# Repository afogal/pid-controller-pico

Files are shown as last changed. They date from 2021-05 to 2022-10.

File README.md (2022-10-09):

# pid-controller-pico

## Setup

### Command

To install prerequisites:

```sh 
sudo pip3 -H install pyqt5 pyqtgraph
```

### Mosquitto (MQTT Broker)

Install mosquitto:

` sudo apt install mosquitto `

To run mosquitto in verbose mode:

` mosquitto -c mosquitto.conf -v `

To ensure it runs on startup (and run it now):

` sudo systemctl enable mosquitto && sudo systemctl start mosquitto `

You also have to copy the `mosquitto.conf`:

` sudo cp mosquitto.conf /etc/mosquitto/mosquitto.conf `

### RPi Pico

To setup the pico fresh, hold down the bootsel button and plug it into the computer. Download the latest adafruit circuitpython uf2 and the latest circuitpython library bundle. (Make sure the versions match, a new major revision is coming out soon, I used the old one, version 6.x.x). Then, drag and drop the circuitpython uf2 to the pico, it'll then remount itself. Now the pico will show up as a drive. Drag and drop the following files to the `lib` folder:

Folders:
* `adafruit_bus_device`
* `adafruit_minimqtt`
* `adafruit_wiznet5k`
* `adafruit_ads1x15`

Files:
* `adafruit_requests.mpy`
* `adafruit_mcp4725.mpy`

As for wiring, the ethernet is wired as follows (diagram and other documentationshows the ethernet interface as WIZ820io, but the prototype that Alex constructed in Spring 2021 used WIZ850io --- JDDM).

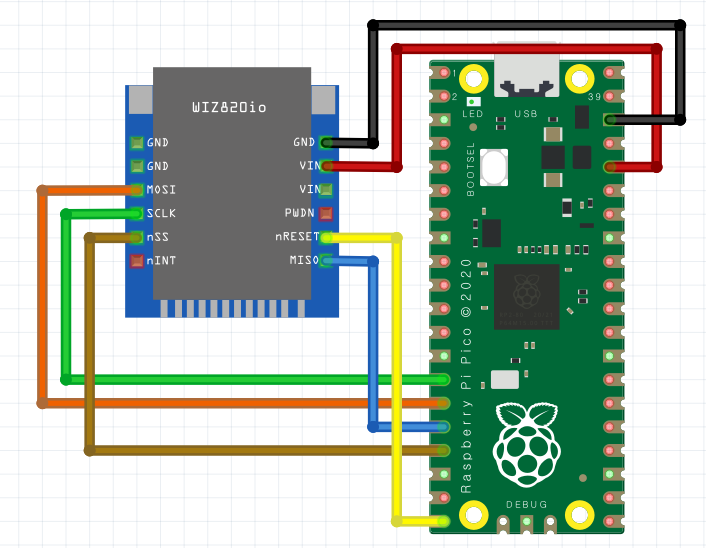
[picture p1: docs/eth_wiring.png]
eth wiring


The i2c bus is wired: pin 26 (GP20) - SDA, pin 27 (GP21) - SCL, and of course, ground to ground and 3v3 to 3v3.

See also: [Schematic](docs/schematic.pdf) and [PCB Layout](docs/pcb.pdf).

In order to program the pico, all you have to do is copy the code.py to the pico, and it will then run that code on boot. One can also install the Thonny editor or the Mu editor. To one can then set Thonny to "Micropython" and point it at the correct serial port (com4 for me) and then you get a REPL running on the pico!

## Settings (defaultSettings dictionary)

The meaning of each entry in the defaultSettings dicitonary is as follows:
* `'setCurrent':0` (Amps) the amount of current to output
* `'setTemp':25` (deg C) the current set temperature to hold
* `'Kc': 6.0787` (W/deg C) PID proportional gain
* `'Ti':330` (sec) PID integration time
* `'Td':0` (sec) PID derivative time (zero gives only a PI control)
* `'I_max':4` (W^2) Maximum value of the I term in PID (best left at max power, 0 -> disabled) 
* `'loadResist':1` (ohm) resistance of the load resistor
* `'maxTemp':150` (deg C) max temperature of the load
* `'maxCurr':2.0` (Amps) max current the load can withstand
* `'maxResVolt':5` (Volt) voltage indicating max resistance
* `'maxRes':13` (kohms) max resistance at max voltage
* `'maxSuppCurrVolt':5` (Volt) the voltage signal that will cause max current from the supply
* `'maxSuppCurr':2` (Amps) max current given by max voltage
* `'thermBeta':3380` (kelvin) thermistor beta
* `'thermR25':10` (kohm) resistance of thermistor at 25 degC
* `'outputToggle':0` are we outputting?
* `'filterHz':1` (Hz) block freqencies higher than this
* `'period':0.016666667` (sec) how often to update PID
* `'constCurr':False` (bool) are we running constant current or PID temperature?
* `'maxErrorLen':100` (int) how many terms to keep around for error
* `'freqAnalysis':False` (bool) outputs current following a cosine wave, only really used for a specific sort of PID tuning
* `'reportMode':'mean'` (one of 'mean', 'latest') report the temperature and current as either the mean of all values since the last or just the latest values
* `'user':'pico'` MQTT username for the PID controller
* `'password':'password'` MQTT password for the PID controller
* `'serverIP':"192.168.0.100"` IP address of the MQTT broker
* `'mqttDelay':5e8` (nsec) how often to poll for mqtt messages and send the current state
* `'mqttReconn":300e8` (nsec) how often to attempt reconnecting to MQTT (is slow, don't attempt often)
* `'lcdRefresh':2.5e8` (nsec) how often to refresh the lcd screen

## User Interface:

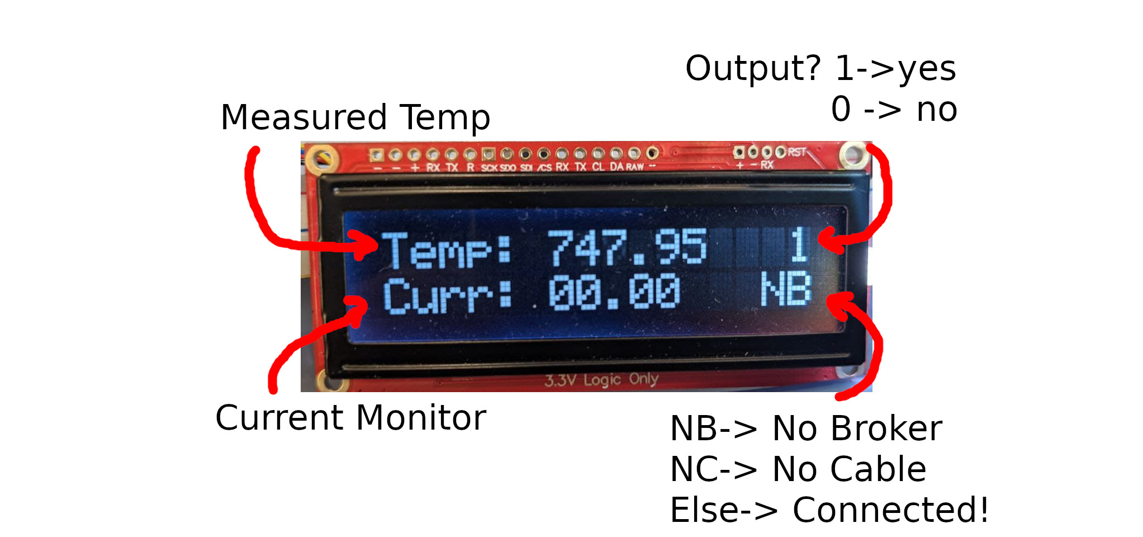
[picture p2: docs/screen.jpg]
screen


## Control UI:

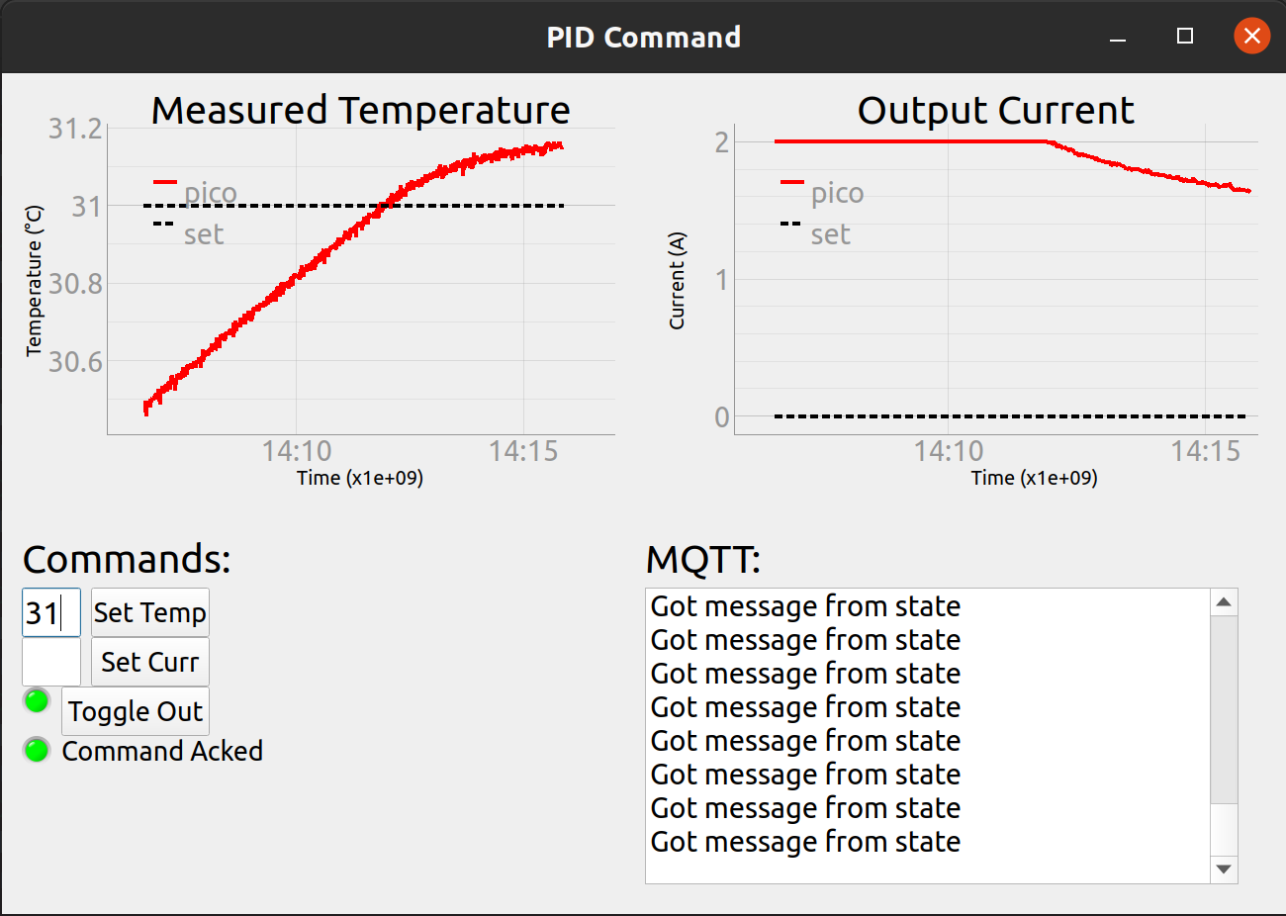
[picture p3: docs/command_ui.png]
control ui


This is the remote command window, featuring set temperature command, set current command, and a toggle output command. For the indicator next to toggle out, red means no current being outputted, and green means current being outputted. The "Command Acked" indicator shows whether or not the pico has recieved and replied to whatever the latest command was, red meaning no, green meaning yes. 

In the bottom right is a text window which updates when acks and messages are recieved, and it will also display errors from trying to type text into the set temp and set curr boxes. 

Finally, in the top is two graphs, they can be panned and zoomed at will, and update with the latest and greatest data from the pico. 

The ui has some configurable parameters, which can be found near the top of [server.py](server/server.py), which include what username the server is, what username the pico is, a password for the mqtt broker, and the IP of the mqtt broker. The broker and command need not be run on the same device, but they can be. 

## Notes:

* printing (which prints to serial) puts a lot of delay (and sometimes doesnt work at all)
* you might have to reconfigure the IP and gatway of the pico depending on network architecture. Run `ipconfig` on windows or `ip addr` on linux to find the relevant details
* the MQTT client keep\_alive is (for some really dumb reason) used as the default pingresp timeout, which means you either flood the broker with ping requests or you wait forever (with no PID processing in the meantime) if the broker ever goes down. I thought 5 seconds would be a fair tradeoff. Even worse: keep\_alive is used as the default recieving timeout, so we can't set it extremely low either. I thought it would be better not to edit and recompile the adafruit library to remedy this, but if desired it would be quite easy.
* for whatever reason, *sometimes* the ADC reads anything greater than 4.1V as exactly 4.1V, I think this is a referencing issue, but it doesn't always come up. This corresponds to a current of 1.64A.

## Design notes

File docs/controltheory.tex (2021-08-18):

\documentclass[11pt, letterpaper]{article}
\usepackage[utf8]{inputenc}
\usepackage{graphicx}
\usepackage{indentfirst}
\usepackage{float}
\setlength{\parindent}{5ex}
\renewcommand{\arraystretch}{1.2}

\usepackage{geometry}

\begin{document}

\begin{titlepage}
    \begin{center}
        \vspace*{1cm}

        \Huge
        \textbf{Control Theory \& PID}

        \vspace{0.5cm}
        \LARGE

        \vspace{1.5cm}

        \textbf{Alexander Fogal}

        \vspace{7.8cm}

        \Large
        For Professor Jim Martin\\
        University of Waterloo\\
        August 13th, 2021

    \end{center}
\end{titlepage}

\tableofcontents

\newpage

\section{Introduction}

Hello! This document is meant to be a brief introduction to the topic of Control Theory and specifically PID process control. This document will make constant referecne to PID temperature control, as not only is it a physically intuitive system, but it is also quite important in the real world. 

Essentially, control theory is exactly what it sounds like: a theoretical background for the automatic control of some system (often referred to as a "plant" or "process"). In order to control the system automatically, some sort of feedback is commonly used. A {\it Closed Loop } system is one which measures its own output to determine what input should be used (feedbacking). Sometimes, the terminology {\it Open Loop} will be used as well, this is simply the negation of the closed loop system: there is no feedback control. This usually implies that the input is held constant, although in general one could apply any arbitrary function as input. 

To set the stage: we have some process we wish to control, some means of measuring it, and some input to control it. The goal of a closed loop system is to stabilize the process at some set point by controlling the input in some fashion related to the output of the system. The controllable property of a system is known as the {\it Process Variable} $PV$, which we wish to hold at the set point, $SP$. We can define the error as simply: $e=SP-PV$, and this is the input to our controller, which implements some control function, and outputs the {\it control signal} (control output) $CO=f(e)=f(SP-PV)$. 

For example, say we have some block of metal we wish to hold at a constant temperature. The set point would be the temperature we wish to hold it at, say, $SP=30^{\circ} C$. The process variable here is the measured temperature of the block, which will change over time: $PV=T_{block}(t)$. Then, we have some controller which will take the error in temperature: $e=SP-PV$ and produce the control signal which will control a heater. 

One quick note on terminology, when we write "controller", we mean any arbitrary control process. This may or may not involve a digital controller or a computer, it could even be analogue circuity! For example, tunable lasers are controlled with an analogue feedback loop. For the example of a heater, it is often better to use a digital controller (e.g., a microcontroller like the Arduino), due to the long times involved with heating. 

\section{Control Theory of Feedback Loops}
\subsection{"P" Control}
The most simple form of feedback control is {\it Proportional} control, in which the control signal  is directly proportional to the error term:

$$ CO = k_P e = k_P ( SP-PV) $$

Assuming $k_P>0$ (in the example of a heater, this is generally true, but there may be cause to use a negative value depending on the system!), the control signal is positive when the process variable is below the set point. This makes sense for the heater system: when the temperature of the block (process variable) is below the set temperature (set point), apply some positive work to the heater in order to produce more heat and thereby increase the process variable to the set point. The units of $k_P$ depend on what exactly is meant to be controlled in this situation. We may wish to control a motor, for which the process variable might have units of degrees (aligning a shaft with a set angle), it could be watts for controlling the motor (delivering power to reach a set speed), and in the case of a heater, it could be watts (delivering power to the heater) or even simply amperes (or volts). For the case of the heater, the units of $k_P$ might be $W/^{\circ} C$.

It is rather easy to see the downfalls of such a simple control process, especially for the example system of a heater: when the process variable (temperature) attains the set point, the control signal becomes zero! For a simple argument of why this would not work for a heater, remember that the subject we wish to heat will be radiating heat at all times as well, so we would never reach the set point if the control signal goes to zero as we get close. An easy solution for this is to add a constant term, but the constant term would depend on the material properties of the system, and the whole point was to make less work for ourselves!

\subsection{"PI" Control}
A slightly more sophisticated form of control would be {\it Proportional (and) Integral} control. This involves adding an integral of the error:

$$ CO = k_P \left (e(t) + \frac{1}{T_I} \int_0^t e(\tau) d\tau \right)$$

The addition of the integral term adds a sort of "momentum" or "memory" to the controller. When the process variable is below the set point, the integral term is growing according to the magnitude of the error, and then it will begin to diminish and settle once the process variable exceeds the set point. The integral term may never reach zero though, it will settle to whatever constant value is required by the system to maintain the set point. As for the units of $T_I$, they would be simply the units we are measuring time in. A physical intuition for $T_I$ (often called the repeat time or integration time) is that it is the amount of time required for the integral term to match the contribution of the proportional term.

For heater control, this is really all that is needed, but it is not too hard to imagine a system where overshooting the set point is unacceptable, or where we cannot afford to wait for the system to settle after reaching the set point. So how do we manage this?

\subsection{"PID" Control}
The "fully featured" control paradigm: {\it Proportional, Integral, Derivative} control. Very powerful and very robust, this paradigm can be used to control all matter of processes. As the name suggests:

$$ CO =  k_P \left( e(t) + \frac{1}{T_I} \int_0^t e(\tau) d\tau + T_D \frac{de}{dt} \right)$$

The addition of the derivative term allows the controller to know how fast the process variable is tending toward the set point and adjust accordingly in order to not overshoot. This would be useful say, for the case of a motor that must turn to a specific angle and no further. The constant $T_D$ is also in units of time. 

\subsection{Properties of PID}
As a quick note, one can pick and choose any of the three PID terms to control the process. As mentioned previously, PI control is sufficient for the case of a heater system. 
\\ \\
One must be careful with their choice of coefficients for PID control though, as PID is a feedback algorithm, it is susceptible to things like feedback loops and oscillation (think mic into an amplified speaker feedbacking). In our heater example, the heat takes time to go from the heater to the thermistor being used to measure and provide feedback. This may not sound like a big problem, but it creates the opportunity for disturbances to build into feedback loops. The phase lag incurred as the heat wave travels from the heater is frequency dependant, and due to the integration term, the system will not settle right away. At low frequencies, the process variable tracks with the control signal, but at higher frequencies, significant phase lag is incurred, resulting in maximum control signal occurring in tandem with maximum change in the process variable and so the process variable will oscillate and not come to equilibrium.

The ratio of the control signal to the process variable amplitude (often expressed as a function of frequency) is referred to as the {\it loop gain} of the process. If we were using only P control, the loop gain would be constant and equal to $k_P$. Under PI control, the gain goes to infinity as frequency goes to zero. The gain is unitless, as the units of the process variable are the inverse of the units of the control signal. This product, often expressed in complex form as a function of frequency, is called the {\it transfer function} of the system. We can model and then analyze this equation in order to mathematically guarantee the stability of our system and the robustness of the control.

\section{Modelling and Analyzing PI Heater Control}
As mentioned in the previous section, we wish to model and analyze the transfer function of the system (the product of the control equation and the process equation) in order to guarantee the stability of our system. 

\subsection{A Quick Aside on the Laplace Transform}
The Laplace transform comes up a lot in Control Theory, it appears when describing linear time invariant systems and the definition of transfer functions. Linear systems are linear in the sense that: $c_1 f(a)+c_2 f(b) = f(c_1 a + c_2 b)$ (in practise this implies that the process transfer function is not dependant on operating point, and behaves the same everywhere), time invariant systems are systems where the output does not depend on when an input was applied (i.e. we can set $t=0$ and do time shifts arbitrarily). For example, most electrical circuits can be approximated by linear and time invariant models. The intuition and physical reasoning for using the Laplace transform in this case is quite hard to appreciate. One can think of the Laplace transform as arising from the idea of impulse responses of the system, or even just that it is convenient for learning properties of the system. For example, the function space that is the output of the Laplace transform allows us to define a norm, and therefore a notion of "closeness" between transfer functions. This is useful to define the robustness of a system: a control scheme that works not just for the subject model, but for "nearby" models as well, can be considered robust. 

Whether one chooses to think of the Laplace transform as a convenient piece of mathematics or as a physically meaningful process, it cannot be ignored in the analysis of systems, particularly since many systems can be approximated as linear and time invariant, and perturbation analyses on these systems are useful as well. To at least convince the reader of its usefulness, any linear and time invariant system can be expressed as:

$$ y(t) = \int_{-\infty}^{\infty} h(t-\tau)u(\tau)d\tau $$

For which the Laplace transform is:

$$ Y(s) = H(s)U(s) $$

simply multiplication. The function $h(t)$ being the impulse response, $H(s)$ being the transfer function, $u(t)$ being the input to the control, $y(t)$ being the output of the control. That is to say, the system is entirely characterized by either the transfer function or the impulse response. We also generally take $s=i\omega$ ($\omega$ being frequency), so the transfer function is a function of frequency only. For more see Olivi, Martine in the reference section.

I will also quickly note that the Z transform is equivalent to the Laplace transform acting on discrete time systems.

\subsection{Modelling PID Control}
The transfer function of the PID control scheme is achieved by taking the Laplace transform of the control signal equation:

$$ H(s) = k_P \left( 1 + \frac{1}{T_I s} + T_d s \right) = k_P \left( 1 + \frac{1}{i \omega T_I } + i \omega T_D  \right) $$

From here on, we will take $T_D = 0$ (PI control only). Our model is therefore: 

$$ H(\omega) = k_P + \frac{k_P}{i\omega T_I} $$

Where the constants are as defined in the PID control scheme.

\subsection{Modelling a Heater System}
Our model for the heater system will consist of two parts: a first order lag, modelled by a low pass RC filter (first term), and a time delay modelled simply by a phase lag (second term). Altogether, this gives us:

$$ G(\omega) = \frac{K}{1+i\omega T_{1}} e^{-i \omega T_d} $$

The constant $K$ (not to be confused with $k_P$) is the loop gain, $T_1$ is first order time lag, and $T_d$ is the time delay. The time delay models the time it takes the heat wave to travel from the heater to the thermistor making the measurements, and the low pass filter models the properties of heat in a medium. 

\subsection{System Model and Stability}
The full model transfer function of our system is now:

$$ H(\omega)G(\omega) = \left( k_P + \frac{k_P}{i \omega T_I}\right)\left( \frac{K}{1+i\omega T_{1}} e^{-i \omega T_d} \right)$$

Now, we can begin to assess the stability of this system using the Nyquist Criterion. Essentially, the Nyquist criterion states that, in order for a system to be stable, it must have a gain of less than unity at a phase of $180^{\circ}$ (and odd multiples, e.g. $540^{\circ},900^{\circ},$ etc.). Graphically, that means that the function must not encircle the point $-1+0i$ in the complex plane. There is more discussion of the related mathematics in Wescott, Tim.

Only one problem, the coefficients in the model are undetermined! For this we have the Ziegler-Nichols design approach.

\subsubsection{Fitting the Heater Model and Determining PID Coefficients}
Essentially, fitting the model is accomplished via graphical construction, but first, we need data. The data in question is called the {\it open loop step response} of the process. This involves setting the input to the process to a constant value, waiting for the process variable to settle, and then increasing the input to some higher value and waiting for it to settle once more. The graph will ideally look like this:

\begin{figure}[H]
    \centering
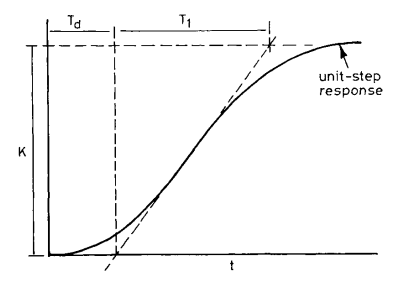
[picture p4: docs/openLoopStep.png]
    
    \caption{ Showing how the coefficients of the model may be determined from step response. Note that it is not important that it be a unit step response, appropriate scaling may be applied instead. }
    \label{fig:openLoopStep}
\end{figure}

In reality, it can be quite a bit messier:

\begin{figure}[H]
    \centering
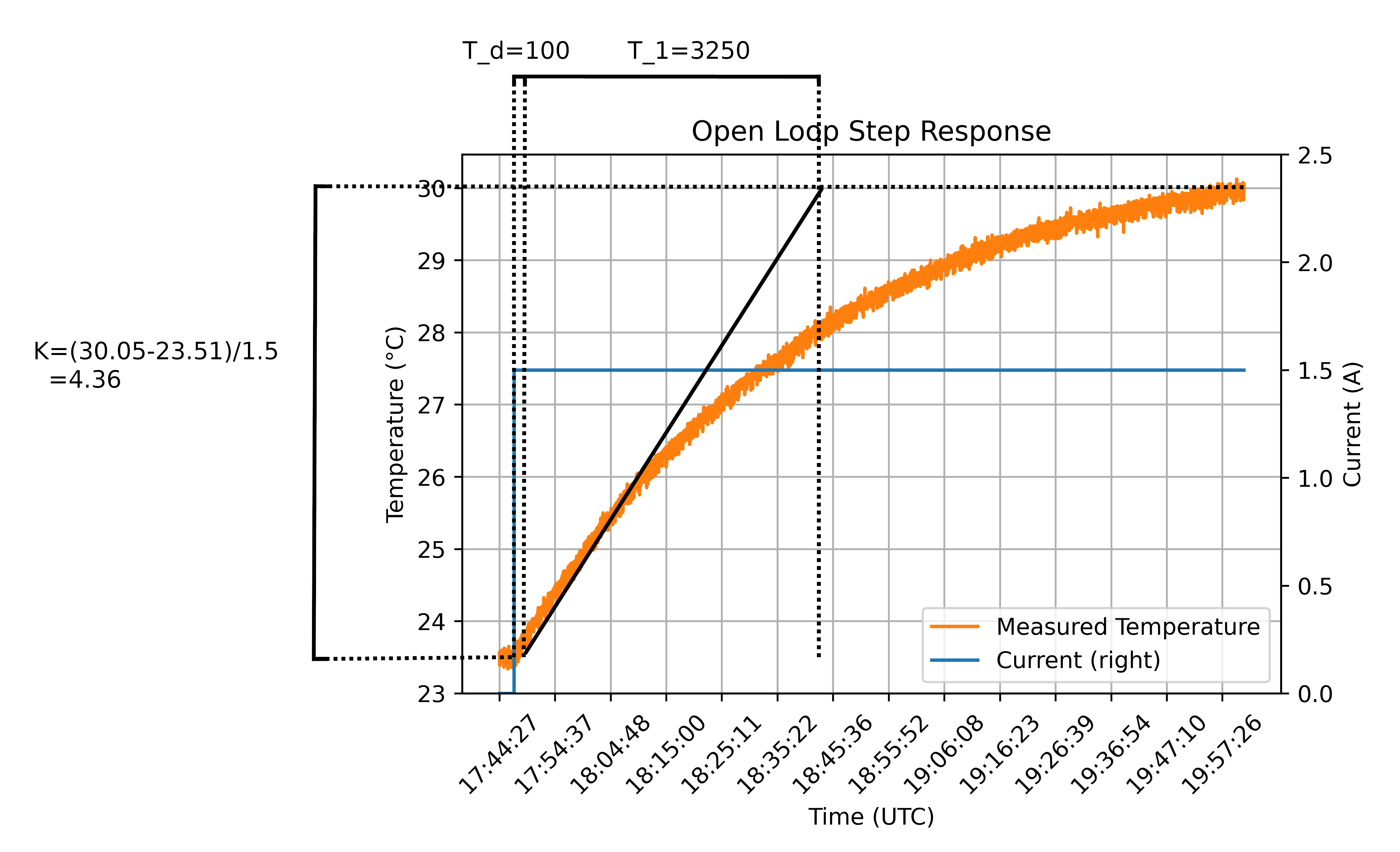
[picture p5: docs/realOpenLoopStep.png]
    
    \caption{ Actually determining coefficients from data. Note that it is verging on impossible to directly use the graph, and digging through the data points will almost certainly be necessary. }
    \label{fig:realOpenLoopStep}
\end{figure}

Given the above values extracted from the data, the following PID coefficients are recommended for stability and optimal control:

\begin{table}[H]
\centering
\begin{tabular}{llll}
     & $k_P$ & $T_I$ & $T_D$  \\[0.3cm] \hline
 P   & $\frac{T_1}{kT_d}$  & -  & - \\[0.3cm]
 PI  & $\frac{0.9 T_1}{KT_d}$  & $3.3T_d$ &  -\\[0.3cm]
 PID & $\frac{1.2 T_1}{KT_d}$  & $2T_d$  & $0.5T_d$
\end{tabular}
\end{table}

\subsubsection{Assessing Stability}
Now that all the coefficients are determined, we can plot the transfer function as a function of frequency in the complex plane. The easiest way to do this is to expand the complex exponentials as a sum of cosines and sines, collect into the form $a(\omega)+ib(\omega)$ and then plot it as a parametric curve, $(a(\omega),b(\omega))$. Having done that gets the following:

\begin{figure}[H]
    \centering
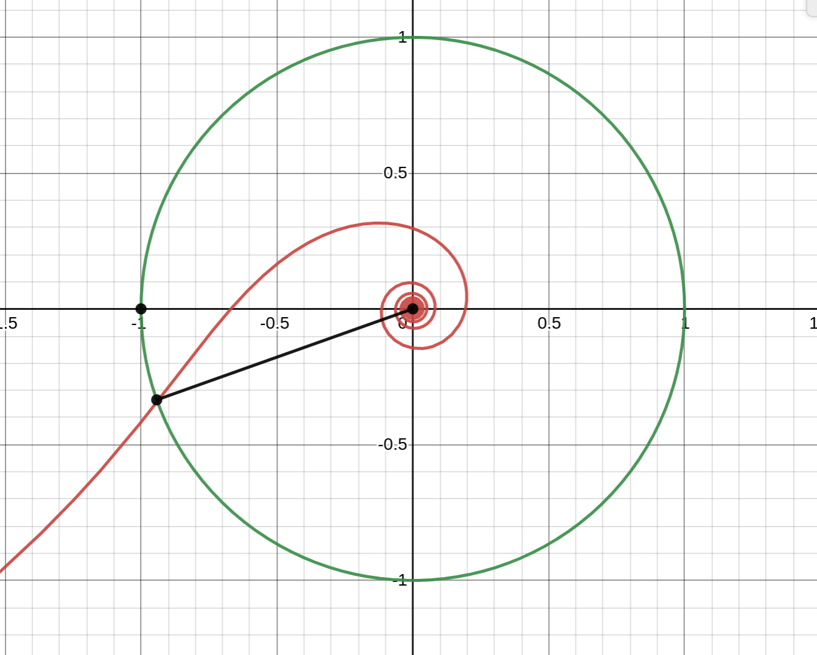
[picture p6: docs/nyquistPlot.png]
    
    \caption{ A plot showing the function as a parametric curve over frequencies $\omega=0...10$ and a unit circle. Note that the curve tends to $-\infty$ on the $y$ axis, which corresponds to the integral having infinite gain (an integrator always contributing a phase of $90^{\circ}$) at zero frequency. Note that the curve does not encircle $-1+0i$ as required for stability. The gain margin here is $3.5$dB and the phase margin is $20^{\circ}$. }
    \label{fig:nyquistPlot}
\end{figure}

There are two factors involved with assessing the stability in relation to the Nyquist criterion: gain margin and phase margin. The gain margin (in dB) is a notion of how far away from oscillation the system will be when the frequency is such that the phase lag is exactly $180^{\circ}$, which is expressed as:

$$ g = 20 \log_{10} \left( -Re(H(\omega^*))\right) $$

In order to assess gain margin, we must first find the frequency corresponding to the closest root to the point $-1+0i$ and then plug that frequency, $\omega^*$, into the real part of the transfer function, and then apply the rest of the above formula.

The phase margin is the angle between the $-x$ axis and the point at which the function intersects the unit circle. In other words, it is the difference in phase between the critical point and where the function is magnitude unity (remember that the function must have less than unity gain at phase $180^{\circ}$). In order to assess phase margin, one must first find the frequency at which the magnitude of the transfer function is 1, i.e., $|H(\omega^*)|=1$ (please excuse my abuse of notation from reusing $\omega^*$ for this, they are not otherwise related).  After that, the transfer function should be put in the form $|H|e^{i\phi}$, and then the phase margin will be $180^{\circ} - \phi$. 

\section{In Practise}
If we have done everything up until now correctly, we will expect that the controller will do a few easily identifiable things. First, when we set the set temperature, the measured temperature should approach and overshoot this, and then exhibit first order decay until settling on the set temperature. Second, this should result in some approximately constant (over short periods of time, since over long periods of time the ambient temperature and therefore the level of current required to maintain a certain temperature, will change) amount of current being delivered.

The closed step response should therefore look like this:

\begin{figure}[H]
    \centering
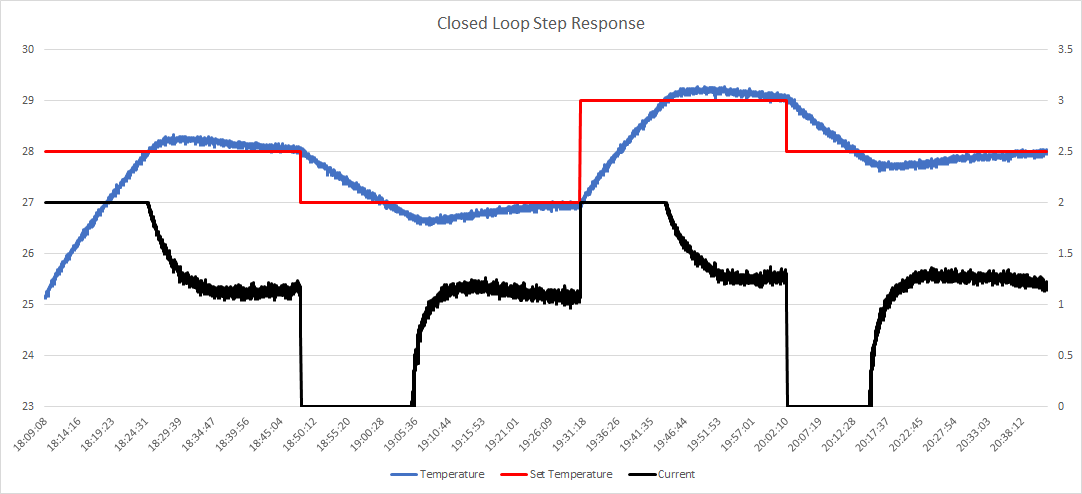
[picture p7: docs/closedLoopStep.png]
    
    \caption{ Forgive my not labelling the axes, the left axis is temperature in Celsius, and the right is current in amperes. The bottom axis is time in UTC. }
    \label{fig:closedLoopStep}
\end{figure}

\newpage
\section{References and Further Reading}
\begin{enumerate}
    \item Jones, Lucas: Practical Implementation of Temperature Control
    \item Martin, James: Notes on Feedback and Oscillations
    \item Olivi, Martine: The Laplace transform in control theory \\ https://www-sop.inria.fr/apics/sbpi/LtransformOlivi.pdf
    \item Forgan, E.M.: On the use of temperature controllers in cryogenics \\ https://doi.org/10.1016/0011-2275(74)90190-8
    \item Wescott, Tim: Applied Control Theory for Embedded Systems
\end{enumerate}

\end{document}

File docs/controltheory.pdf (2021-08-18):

# Control Theory & PID

## Alexander Fogal

## For Professor Jim Martin University of Waterloo August 13th, 2021

## Contents

1 Introduction | 2
2 Control Theory of Feedback Loops | 2
3 Modelling and Analyzing PI Heater Control | 5
4 In Practise | 10
5 References and Further Reading | 11

1

## 1 Introduction

Hello! This document is meant to be a brief introduction to the topic of Control Theory and specifically PID process control. This document will make constant referecne to PID temperature control, as not only is it a physically intuitive system, but it is also quite important in the real world.
Essentially, control theory is exactly what it sounds like: a theoretical background for the automatic control of some system (often referred to as a ”plant” or ”process”). In order to control the system automatically, some sort of feedback is commonly used. A Closed Loop system is one which measures its own output to determine what input should be used (feedbacking). Sometimes, the terminology Open Loop will be used as well, this is simply the negation of the closed loop system: there is no feedback control. This usually implies that the input is held constant, although in general one could apply any arbitrary function as input.
To set the stage: we have some process we wish to control, some means of measuring it, and some input to control it. The goal of a closed loop system is to stabilize the process at some set point by controlling the input in some fashion related to the output of the system. The controllable property of a system is known as the Process Variable P V , which we wish to hold at the set point, SP. We can define the error as simply: e = SP −P V , and this is the input to our controller, which implements some control function, and outputs the control signal (control output) CO = f(e) = f(SP − P V ).
For example, say we have some block of metal we wish to hold at a constant temperature. The set point would be the temperature we wish to hold it at, say, SP = 30◦C. The process variable here is the measured temperature of the block, which will change over time: P V = Tblock(t). Then, we have some controller which will take the error in temperature: e = SP − P V and produce the control signal which will control a heater. One quick note on terminology, when we write ”controller”, we mean any arbitrary control process. This may or may not involve a digital controller or a computer, it could even be analogue circuity! For example, tunable lasers are controlled with an analogue feedback loop. For the example of a heater, it is often better to use a digital controller (e.g., a microcontroller like the Arduino), due to the long times involved with heating.

## 2 Control Theory of Feedback Loops

2.1 ”P” Control

The most simple form of feedback control is Proportional control, in which the control signal is directly proportional to the error term:

CO = kP e = kP (SP − P V )

2

Assuming kP > 0 (in the example of a heater, this is generally true, but there may be cause to use a negative value depending on the system!), the control signal is positive when the process variable is below the set point. This makes sense for the heater system: when the temperature of the block (process variable) is below the set temperature (set point), apply some positive work to the heater in order to produce more heat and thereby increase the process variable to the set point. The units of kP depend on what exactly is meant to be controlled in this situation. We may wish to control a motor, for which the process variable might have units of degrees (aligning a shaft with a set angle), it could be watts for controlling the motor (delivering power to reach a set speed), and in the case of a heater, it could be watts (delivering power to the heater) or even simply amperes (or volts). For the case of the heater, the units of kP might be W/◦C.
It is rather easy to see the downfalls of such a simple control process, especially for the example system of a heater: when the process variable (temperature) attains the set point, the control signal becomes zero! For a simple argument of why this would not work for a heater, remember that the subject we wish to heat will be radiating heat at all times as well, so we would never reach the set point if the control signal goes to zero as we get close. An easy solution for this is to add a constant term, but the constant term would depend on the material properties of the system, and the whole point was to make less work for ourselves!

2.2 ”PI” Control

A slightly more sophisticated form of control would be Proportional (and) Integral control. This involves adding an integral of the error:

CO = kP

e(t) + 1
TI

Z t

0

e(τ )dτ

The addition of the integral term adds a sort of ”momentum” or ”memory” to the controller. When the process variable is below the set point, the integral term is growing according to the magnitude of the error, and then it will begin to diminish and settle once the process variable exceeds the set point. The integral term may never reach zero though, it will settle to whatever constant value is required by the system to maintain the set point. As for the units of TI , they would be simply the units we are measuring time in. A physical intuition for TI (often called the repeat time or integration time) is that it is the amount of time required for the integral term to match the contribution of the proportional term. For heater control, this is really all that is needed, but it is not too hard to imagine a system where overshooting the set point is unacceptable, or where we cannot afford to wait for the system to settle after reaching the set point. So how do we manage this?

3

2.3 ”PID” Control

The ”fully featured” control paradigm: Proportional, Integral, Derivative control. Very powerful and very robust, this paradigm can be used to control all matter of processes. As the name suggests:

CO = kP

e(t) + 1
TI

Z t

0

e(τ )dτ + TD

de
dt

The addition of the derivative term allows the controller to know how fast the process variable is tending toward the set point and adjust accordingly in order to not overshoot. This would be useful say, for the case of a motor that must turn to a specific angle and no further. The constant TD is also in units of time.

### 2.4 Properties of PID

As a quick note, one can pick and choose any of the three PID terms to control the process. As mentioned previously, PI control is sufficient for the case of a heater system.

One must be careful with their choice of coefficients for PID control though, as PID is a feedback algorithm, it is susceptible to things like feedback loops and oscillation (think mic into an amplified speaker feedbacking). In our heater example, the heat takes time to go from the heater to the thermistor being used to measure and provide feedback. This may not sound like a big problem, but it creates the opportunity for disturbances to build into feedback loops. The phase lag incurred as the heat wave travels from the heater is frequency dependant, and due to the integration term, the system will not settle right away. At low frequencies, the process variable tracks with the control signal, but at higher frequencies, significant phase lag is incurred, resulting in maximum control signal occurring in tandem with maximum change in the process variable and so the process variable will oscillate and not come to equilibrium.
The ratio of the control signal to the process variable amplitude (often expressed as a function of frequency) is referred to as the loop gain of the process. If we were using only P control, the loop gain would be constant and equal to kP . Under PI control, the gain goes to infinity as frequency goes to zero. The gain is unitless, as the units of the process variable are the inverse of the units of the control signal. This product, often expressed in complex form as a function of frequency, is called the transfer function of the system. We can model and then analyze this equation in order to mathematically guarantee the stability of our system and the robustness of the control.

4

## 3 Modelling and Analyzing PI Heater Control

As mentioned in the previous section, we wish to model and analyze the transfer function of the system (the product of the control equation and the process equation) in order to guarantee the stability of our system.

### 3.1 A Quick Aside on the Laplace Transform

The Laplace transform comes up a lot in Control Theory, it appears when describing linear time invariant systems and the definition of transfer functions. Linear systems are linear in the sense that: c1f(a) + c2f(b) = f(c1a + c2b) (in practise this implies that the process transfer function is not dependant on operating point, and behaves the same everywhere), time invariant systems are systems where the output does not depend on when an input was applied (i.e. we can set t = 0 and do time shifts arbitrarily). For example, most electrical circuits can be approximated by linear and time invariant models. The intuition and physical reasoning for using the Laplace transform in this case is quite hard to appreciate. One can think of the Laplace transform as arising from the idea of impulse responses of the system, or even just that it is convenient for learning properties of the system. For example, the function space that is the output of the Laplace transform allows us to define a norm, and therefore a notion of ”closeness” between transfer functions. This is useful to define the robustness of a system: a control scheme that works not just for the subject model, but for ”nearby” models as well, can be considered robust. Whether one chooses to think of the Laplace transform as a convenient piece of mathematics or as a physically meaningful process, it cannot be ignored in the analysis of systems, particularly since many systems can be approximated as linear and time invariant, and perturbation analyses on these systems are useful as well. To at least convince the reader of its usefulness, any linear and time invariant system can be expressed as:

y(t) = Z ∞

−∞

h(t − τ )u(τ )dτ

For which the Laplace transform is:

Y (s) = H(s)U(s)

simply multiplication. The function h(t) being the impulse response, H(s) being the transfer function, u(t) being the input to the control, y(t) being the output of the control. That is to say, the system is entirely characterized by either the transfer function or the impulse response. We also generally take s = iω (ω being frequency), so the transfer function is a function of frequency only. For more see Olivi, Martine in the reference section.
I will also quickly note that the Z transform is equivalent to the Laplace transform acting on discrete time systems.

5

### 3.2 Modelling PID Control

The transfer function of the PID control scheme is achieved by taking the Laplace transform of the control signal equation:

H(s) = kP

1 +

1
TIs

+ Tds

= kP
1 +

1
iωTI

+ iωTD

From here on, we will take TD = 0 (PI control only). Our model is therefore:

H(ω) = kP +

kP
iωTI
Where the constants are as defined in the PID control scheme.

### 3.3 Modelling a Heater System

Our model for the heater system will consist of two parts: a first order lag, modelled by a low pass RC filter (first term), and a time delay modelled simply by a phase lag (second term). Altogether, this gives us:

G(ω) = K 1 + iωT1
e

−iωTd

The constant K (not to be confused with kP ) is the loop gain, T1 is first order time lag, and Td is the time delay. The time delay models the time it takes the heat wave to travel from the heater to the thermistor making the measurements, and the low pass filter models the properties of heat in a medium.

### 3.4 System Model and Stability

The full model transfer function of our system is now:

H(ω)G(ω) = kP + | kP iωTI

K
1 + iωT1

e

−iωTd

Now, we can begin to assess the stability of this system using the Nyquist Criterion. Essentially, the Nyquist criterion states that, in order for a system to be stable, it must have a gain of less than unity at a phase of 180◦

(and odd multiples, e.g. 540◦

, 900◦
,
etc.). Graphically, that means that the function must not encircle the point −1 + 0i in the complex plane. There is more discussion of the related mathematics in Wescott, Tim. Only one problem, the coefficients in the model are undetermined! For this we have the Ziegler-Nichols design approach.

6

### 3.4.1 Fitting the Heater Model and Determining PID Coefficients

Essentially, fitting the model is accomplished via graphical construction, but first, we need data. The data in question is called the open loop step response of the process. This involves setting the input to the process to a constant value, waiting for the process variable to settle, and then increasing the input to some higher value and waiting for it to settle once more. The graph will ideally look like this:


Figure 1: Showing how the coefficients of the model may be determined from step response. Note that it is not important that it be a unit step response, appropriate scaling may be applied instead.

In reality, it can be quite a bit messier:

7


Figure 2: Actually determining coefficients from data. Note that it is verging on impossible to directly use the graph, and digging through the data points will almost certainly be necessary.

Given the above values extracted from the data, the following PID coefficients are recommended for stability and optimal control:

kP | TI | TD

P

T1
kTd
PI | 0.9T1
KTd | 3.3Td | -
PID | 1.2T1
KTd | 2Td | 0.5Td

8

### 3.4.2 Assessing Stability

Now that all the coefficients are determined, we can plot the transfer function as a function of frequency in the complex plane. The easiest way to do this is to expand the complex exponentials as a sum of cosines and sines, collect into the form a(ω) + ib(ω) and then plot it as a parametric curve, (a(ω), b(ω)). Having done that gets the following:

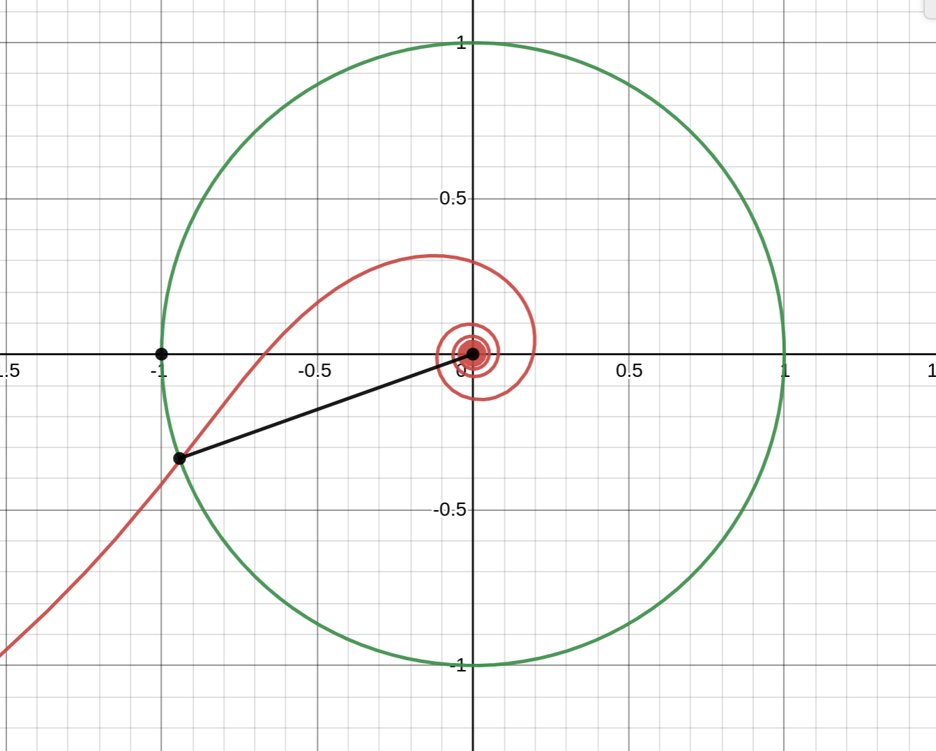
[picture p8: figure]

Figure 3: A plot showing the function as a parametric curve over frequencies ω = 0...10 and a unit circle. Note that the curve tends to −∞ on the y axis, which corresponds to the integral having infinite gain (an integrator always contributing a phase of 90◦
) at zero
frequency. Note that the curve does not encircle −1 + 0i as required for stability. The gain margin here is 3.5dB and the phase margin is 20◦

There are two factors involved with assessing the stability in relation to the Nyquist criterion: gain margin and phase margin. The gain margin (in dB) is a notion of how far away from oscillation the system will be when the frequency is such that the phase lag is exactly 180◦
, which is expressed as:

g = 20 log10 (−Re(H(ω

∗
)))

In order to assess gain margin, we must first find the frequency corresponding to the

9

closest root to the point −1 + 0i and then plug that frequency, ω

∗
, into the real part of the transfer function, and then apply the rest of the above formula.
The phase margin is the angle between the −x axis and the point at which the function intersects the unit circle. In other words, it is the difference in phase between the critical point and where the function is magnitude unity (remember that the function must have less than unity gain at phase 180◦
). In order to assess phase margin, one must first find the frequency at which the magnitude of the transfer function is 1, i.e., |H(ω

∗
)| = 1 (please
excuse my abuse of notation from reusing ω

∗
for this, they are not otherwise related). After that, the transfer function should be put in the form |H|e iφ, and then the phase margin will be 180◦ − φ.

## 4 In Practise

If we have done everything up until now correctly, we will expect that the controller will do a few easily identifiable things. First, when we set the set temperature, the measured temperature should approach and overshoot this, and then exhibit first order decay until settling on the set temperature. Second, this should result in some approximately constant (over short periods of time, since over long periods of time the ambient temperature and therefore the level of current required to maintain a certain temperature, will change) amount of current being delivered.
The closed step response should therefore look like this:

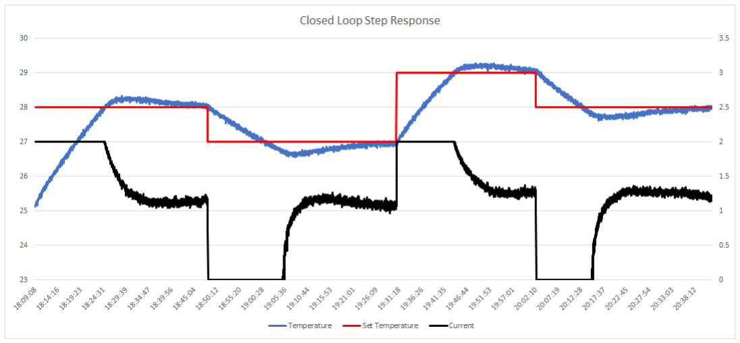
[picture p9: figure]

Figure 4: Forgive my not labelling the axes, the left axis is temperature in Celsius, and the right is current in amperes. The bottom axis is time in UTC.

10

## 5 References and Further Reading

1. Jones, Lucas: Practical Implementation of Temperature Control
2. Martin, James: Notes on Feedback and Oscillations
3. Olivi, Martine: The Laplace transform in control theory https://www-sop.inria.fr/apics/sbpi/LtransformOlivi.pdf
4. Forgan, E.M.: On the use of temperature controllers in cryogenics https://doi.org/10.1016/0011-2275(74)90190-8
5. Wescott, Tim: Applied Control Theory for Embedded Systems

11

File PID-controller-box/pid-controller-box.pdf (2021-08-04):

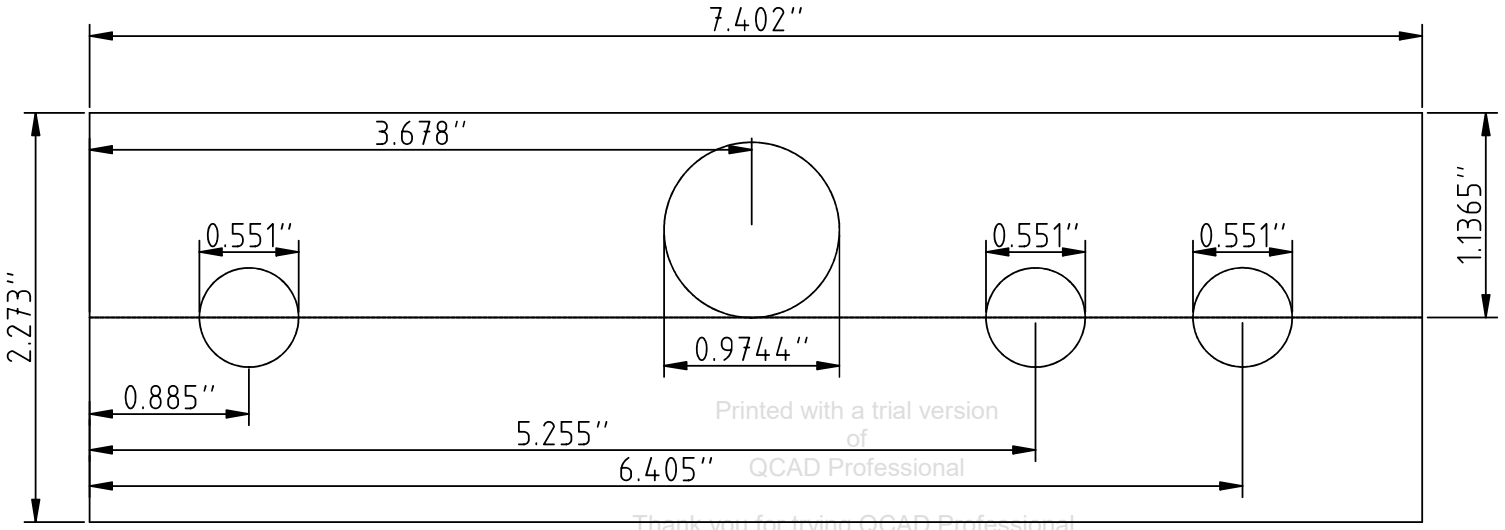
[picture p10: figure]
Printed with a trial version of QCAD Professional

Thank you for trying QCAD Professional.

This trial version allows you to try QCAD Professional before you decide if you want to buy it. It is not intended for production use.

To start using QCAD Professional productively, please buy a full version for a small fee

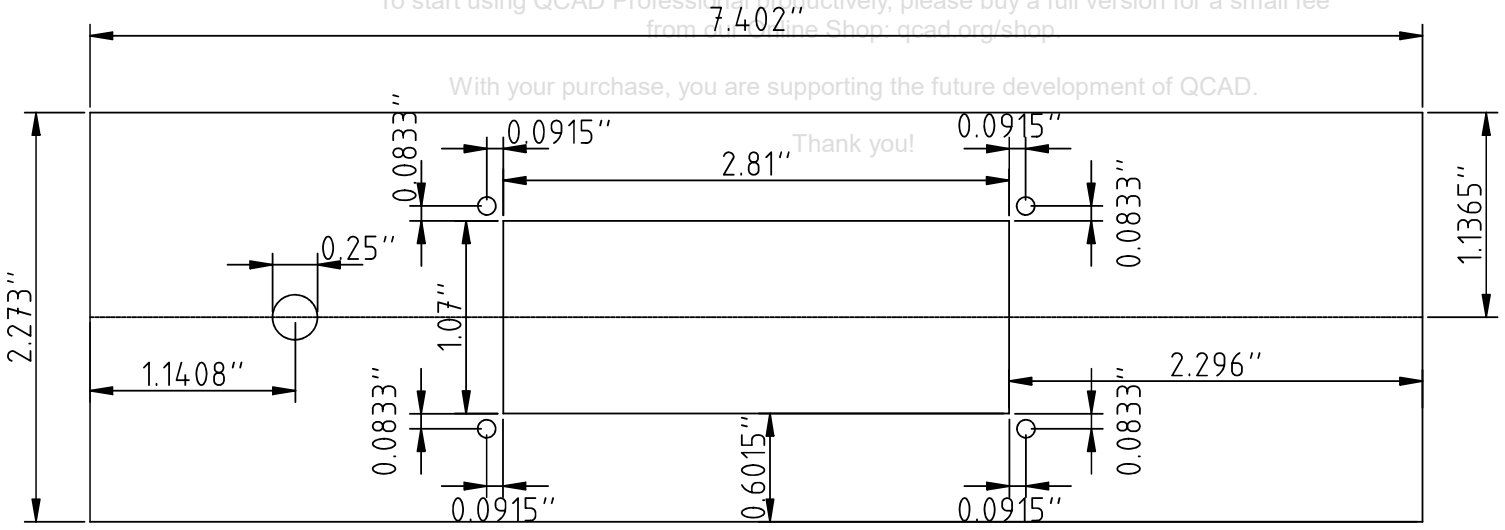
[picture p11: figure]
from our Online Shop: qcad.org/shop.; Thank you!

With your purchase, you are supporting the future development of QCAD.

# Back, open side up

# Front, open side up

# * All screw holes on front have diameter 0.1" * All 0.551" holes on the back are meant to fit a 0.5" 20 threaded

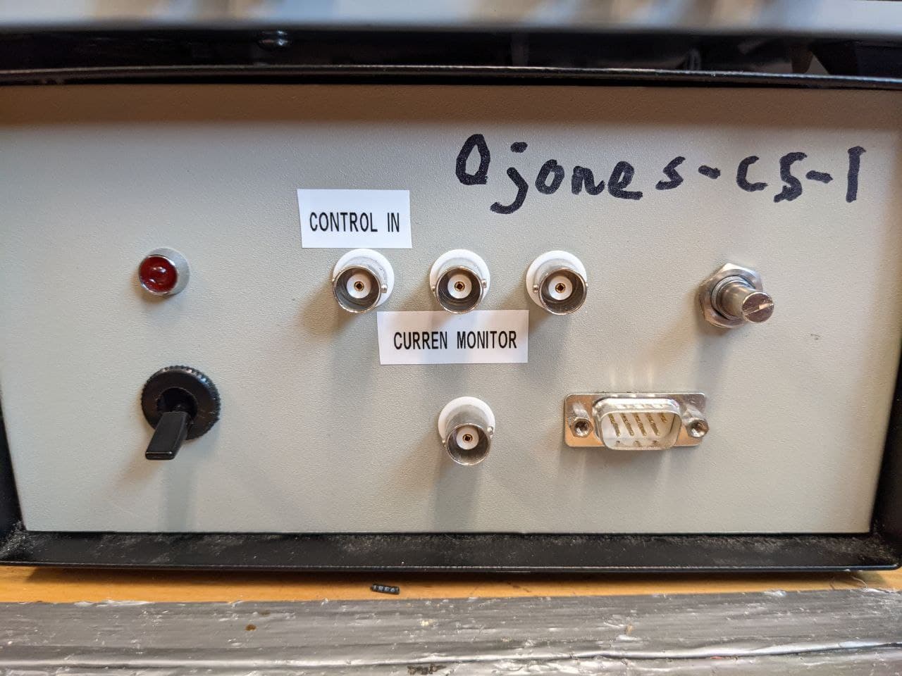
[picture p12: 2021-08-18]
docs/currentSourceConnections.jpg

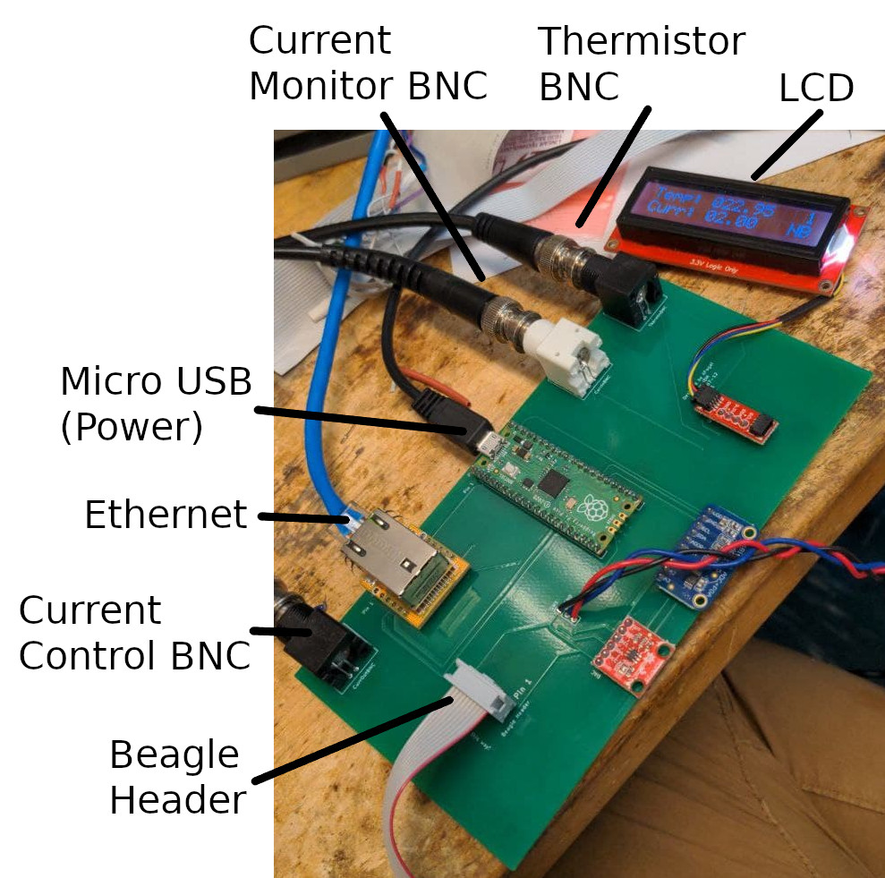
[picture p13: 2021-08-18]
docs/controllerConnections.jpg

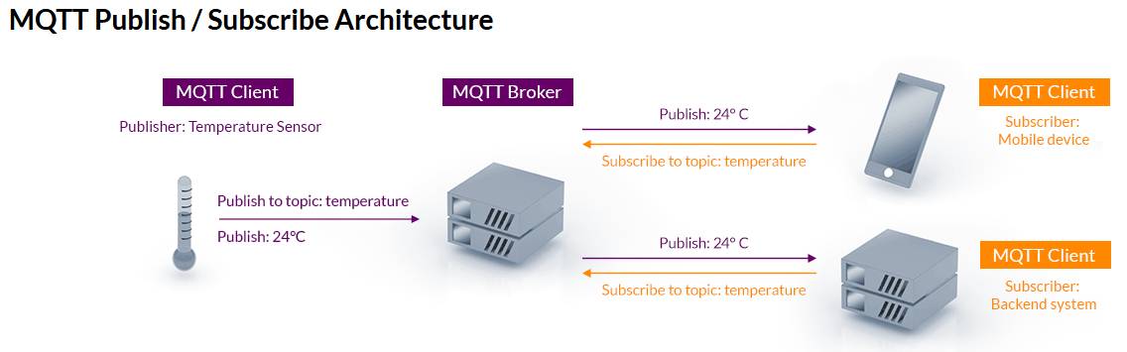
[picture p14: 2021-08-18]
docs/mqttArch.png

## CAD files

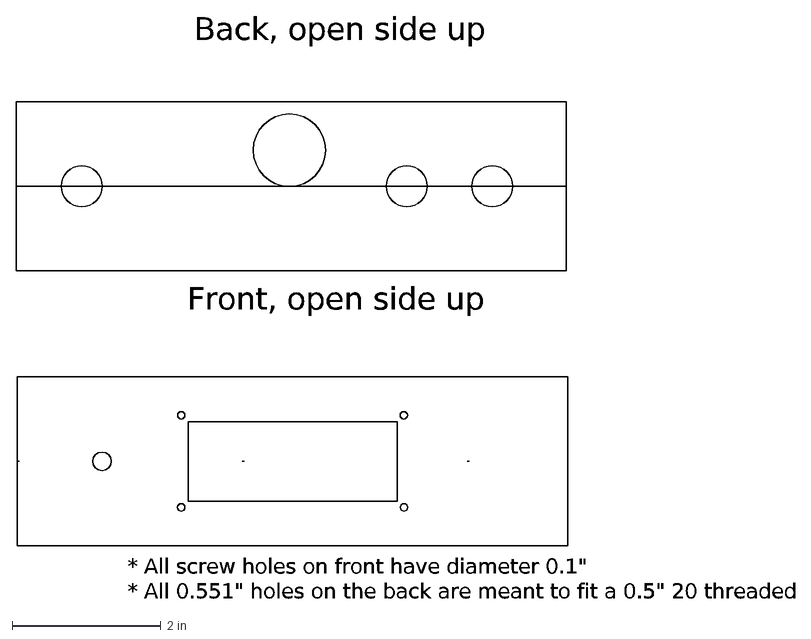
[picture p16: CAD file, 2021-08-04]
PID-controller-box/pid-controller-box.dxf
Back, open side up
Front, open side up
* All screw holes on front have diameter 0.1" * All 0.551" holes on the back are meant to fit a 0.5" 20 threaded

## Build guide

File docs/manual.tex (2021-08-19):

\documentclass[11pt, letterpaper]{article}
\usepackage[utf8]{inputenc}
\usepackage{graphicx}
\usepackage{indentfirst}
\usepackage{float}
\setlength{\parindent}{5ex}
\renewcommand{\arraystretch}{1.2}

\usepackage{geometry}

\begin{document}

\begin{titlepage}
    \begin{center}
        \vspace*{1cm}

        \Huge
        \textbf{Control Theory \& PID}

        \vspace{0.5cm}
        \LARGE

        \vspace{1.5cm}

        \textbf{Alexander Fogal}

        \vspace{7.8cm}

        \Large
        For Professor Jim Martin\\
        University of Waterloo\\
        August 13th, 2021

    \end{center}
\end{titlepage}

\tableofcontents

\newpage

\section{Introduction}

Hello! This document is meant to be a brief introduction to the topic of Control Theory and specifically PID process control. This document will make constant referecne to PID temperature control, as not only is it a physically intuitive system, but it is also quite important in the real world. 

Essentially, control theory is exactly what it sounds like: a theoretical background for the automatic control of some system (often referred to as a "plant" or "process"). In order to control the system automatically, some sort of feedback is commonly used. A {\it Closed Loop } system is one which measures its own output to determine what input should be used (feedbacking). Sometimes, the terminology {\it Open Loop} will be used as well, this is simply the negation of the closed loop system: there is no feedback control. This usually implies that the input is held constant, although in general one could apply any arbitrary function as input. 

To set the stage: we have some process we wish to control, some means of measuring it, and some input to control it. The goal of a closed loop system is to stabilize the process at some set point by controlling the input in some fashion related to the output of the system. The controllable property of a system is known as the {\it Process Variable} $PV$, which we wish to hold at the set point, $SP$. We can define the error as simply: $e=SP-PV$, and this is the input to our controller, which implements some control function, and outputs the {\it control signal} (control output) $CO=f(e)=f(SP-PV)$. 

For example, say we have some block of metal we wish to hold at a constant temperature. The set point would be the temperature we wish to hold it at, say, $SP=30^{\circ} C$. The process variable here is the measured temperature of the block, which will change over time: $PV=T_{block}(t)$. Then, we have some controller which will take the error in temperature: $e=SP-PV$ and produce the control signal which will control a heater. 

One quick note on terminology, when we write "controller", we mean any arbitrary control process. This may or may not involve a digital controller or a computer, it could even be analogue circuity! For example, tunable lasers are controlled with an analogue feedback loop. For the example of a heater, it is often better to use a digital controller (e.g., a microcontroller like the Arduino), due to the long times involved with heating. 

\section{Control Theory of Feedback Loops}
\subsection{"P" Control}
The most simple form of feedback control is {\it Proportional} control, in which the control signal  is directly proportional to the error term:

$$ CO = k_P e = k_P ( SP-PV) $$

Assuming $k_P>0$ (in the example of a heater, this is generally true, but there may be cause to use a negative value depending on the system!), the control signal is positive when the process variable is below the set point. This makes sense for the heater system: when the temperature of the block (process variable) is below the set temperature (set point), apply some positive work to the heater in order to produce more heat and thereby increase the process variable to the set point. The units of $k_P$ depend on what exactly is meant to be controlled in this situation. We may wish to control a motor, for which the process variable might have units of degrees (aligning a shaft with a set angle), it could be watts for controlling the motor (delivering power to reach a set speed), and in the case of a heater, it could be watts (delivering power to the heater) or even simply amperes (or volts). For the case of the heater, the units of $k_P$ might be $W/^{\circ} C$.

It is rather easy to see the downfalls of such a simple control process, especially for the example system of a heater: when the process variable (temperature) attains the set point, the control signal becomes zero! For a simple argument of why this would not work for a heater, remember that the subject we wish to heat will be radiating heat at all times as well, so we would never reach the set point if the control signal goes to zero as we get close. An easy solution for this is to add a constant term, but the constant term would depend on the material properties of the system, and the whole point was to make less work for ourselves!

\subsection{"PI" Control}
A slightly more sophisticated form of control would be {\it Proportional (and) Integral} control. This involves adding an integral of the error:

$$ CO = k_P \left (e(t) + \frac{1}{T_I} \int_0^t e(\tau) d\tau \right)$$

The addition of the integral term adds a sort of "momentum" or "memory" to the controller. When the process variable is below the set point, the integral term is growing according to the magnitude of the error, and then it will begin to diminish and settle once the process variable exceeds the set point. The integral term may never reach zero though, it will settle to whatever constant value is required by the system to maintain the set point. As for the units of $T_I$, they would be simply the units we are measuring time in. A physical intuition for $T_I$ (often called the repeat time or integration time) is that it is the amount of time required for the integral term to match the contribution of the proportional term.

For heater control, this is really all that is needed, but it is not too hard to imagine a system where overshooting the set point is unacceptable, or where we cannot afford to wait for the system to settle after reaching the set point. So how do we manage this?

\subsection{"PID" Control}
The "fully featured" control paradigm: {\it Proportional, Integral, Derivative} control. Very powerful and very robust, this paradigm can be used to control all matter of processes. As the name suggests:

$$ CO =  k_P \left( e(t) + \frac{1}{T_I} \int_0^t e(\tau) d\tau + T_D \frac{de}{dt} \right)$$

The addition of the derivative term allows the controller to know how fast the process variable is tending toward the set point and adjust accordingly in order to not overshoot. This would be useful say, for the case of a motor that must turn to a specific angle and no further. The constant $T_D$ is also in units of time. 

\subsection{Properties of PID}
As a quick note, one can pick and choose any of the three PID terms to control the process. As mentioned previously, PI control is sufficient for the case of a heater system. 
\\ \\
One must be careful with their choice of coefficients for PID control though, as PID is a feedback algorithm, it is susceptible to things like feedback loops and oscillation (think mic into an amplified speaker feedbacking). In our heater example, the heat takes time to go from the heater to the thermistor being used to measure and provide feedback. This may not sound like a big problem, but it creates the opportunity for disturbances to build into feedback loops. The phase lag incurred as the heat wave travels from the heater is frequency dependant, and due to the integration term, the system will not settle right away. At low frequencies, the process variable tracks with the control signal, but at higher frequencies, significant phase lag is incurred, resulting in maximum control signal occurring in tandem with maximum change in the process variable and so the process variable will oscillate and not come to equilibrium.

The ratio of the control signal to the process variable amplitude (often expressed as a function of frequency) is referred to as the {\it loop gain} of the process. If we were using only P control, the loop gain would be constant and equal to $k_P$. Under PI control, the gain goes to infinity as frequency goes to zero. The gain is unitless, as the units of the process variable are the inverse of the units of the control signal. This product, often expressed in complex form as a function of frequency, is called the {\it transfer function} of the system. We can model and then analyze this equation in order to mathematically guarantee the stability of our system and the robustness of the control.

\section{Modelling and Analyzing PI Heater Control}
As mentioned in the previous section, we wish to model and analyze the transfer function of the system (the product of the control equation and the process equation) in order to guarantee the stability of our system. 

\subsection{A Quick Aside on the Laplace Transform}
The Laplace transform comes up a lot in Control Theory, it appears when describing linear time invariant systems and the definition of transfer functions. Linear systems are linear in the sense that: $c_1 f(a)+c_2 f(b) = f(c_1 a + c_2 b)$ (in practise this implies that the process transfer function is not dependant on operating point, and behaves the same everywhere), time invariant systems are systems where the output does not depend on when an input was applied (i.e. we can set $t=0$ and do time shifts arbitrarily). For example, most electrical circuits can be approximated by linear and time invariant models. The intuition and physical reasoning for using the Laplace transform in this case is quite hard to appreciate. One can think of the Laplace transform as arising from the idea of impulse responses of the system, or even just that it is convenient for learning properties of the system. For example, the function space that is the output of the Laplace transform allows us to define a norm, and therefore a notion of "closeness" between transfer functions. This is useful to define the robustness of a system: a control scheme that works not just for the subject model, but for "nearby" models as well, can be considered robust. 

Whether one chooses to think of the Laplace transform as a convenient piece of mathematics or as a physically meaningful process, it cannot be ignored in the analysis of systems, particularly since many systems can be approximated as linear and time invariant, and perturbation analyses on these systems are useful as well. To at least convince the reader of its usefulness, any linear and time invariant system can be expressed as:

$$ y(t) = \int_{-\infty}^{\infty} h(t-\tau)u(\tau)d\tau $$

For which the Laplace transform is:

$$ Y(s) = H(s)U(s) $$

simply multiplication. The function $h(t)$ being the impulse response, $H(s)$ being the transfer function, $u(t)$ being the input to the control, $y(t)$ being the output of the control. That is to say, the system is entirely characterized by either the transfer function or the impulse response. We also generally take $s=i\omega$ ($\omega$ being frequency), so the transfer function is a function of frequency only. For more see Olivi, Martine in the reference section.

I will also quickly note that the Z transform is equivalent to the Laplace transform acting on discrete time systems.

\subsection{Modelling PID Control}
The transfer function of the PID control scheme is achieved by taking the Laplace transform of the control signal equation:

$$ H(s) = k_P \left( 1 + \frac{1}{T_I s} + T_d s \right) = k_P \left( 1 + \frac{1}{i \omega T_I } + i \omega T_D  \right) $$

From here on, we will take $T_D = 0$ (PI control only). Our model is therefore: 

$$ H(\omega) = k_P + \frac{k_P}{i\omega T_I} $$

Where the constants are as defined in the PID control scheme.

\subsection{Modelling a Heater System}
Our model for the heater system will consist of two parts: a first order lag, modelled by a low pass RC filter (first term), and a time delay modelled simply by a phase lag (second term). Altogether, this gives us:

$$ G(\omega) = \frac{K}{1+i\omega T_{1}} e^{-i \omega T_d} $$

The constant $K$ (not to be confused with $k_P$) is the loop gain, $T_1$ is first order time lag, and $T_d$ is the time delay. The time delay models the time it takes the heat wave to travel from the heater to the thermistor making the measurements, and the low pass filter models the properties of heat in a medium. 

\subsection{System Model and Stability}
The full model transfer function of our system is now:

$$ H(\omega)G(\omega) = \left( k_P + \frac{k_P}{i \omega T_I}\right)\left( \frac{K}{1+i\omega T_{1}} e^{-i \omega T_d} \right)$$

Now, we can begin to assess the stability of this system using the Nyquist Criterion. Essentially, the Nyquist criterion states that, in order for a system to be stable, it must have a gain of less than unity at a phase of $180^{\circ}$ (and odd multiples, e.g. $540^{\circ},900^{\circ},$ etc.). Graphically, that means that the function must not encircle the point $-1+0i$ in the complex plane. There is more discussion of the related mathematics in Wescott, Tim.

Only one problem, the coefficients in the model are undetermined! For this we have the Ziegler-Nichols design approach.

\subsubsection{Fitting the Heater Model and Determining PID Coefficients}
Essentially, fitting the model is accomplished via graphical construction, but first, we need data. The data in question is called the {\it open loop step response} of the process. This involves setting the input to the process to a constant value, waiting for the process variable to settle, and then increasing the input to some higher value and waiting for it to settle once more. The graph will ideally look like this:

\begin{figure}[H]
    \centering
    
    \caption{ Showing how the coefficients of the model may be determined from step response. Note that it is not important that it be a unit step response, appropriate scaling may be applied instead. Figure taken from Leigh, J.R. figure 11.1.}
    \label{fig:openLoopStep}
\end{figure}

In reality, it can be quite a bit messier:

\begin{figure}[H]
    \centering
    
    \caption{ Actually determining coefficients from data. Note that it is verging on impossible to directly use the graph, and digging through the data points will almost certainly be necessary. }
    \label{fig:realOpenLoopStep}
\end{figure}

Given the above values extracted from the data, the following PID coefficients are recommended for stability and optimal control:

\begin{table}[H]
\centering
\begin{tabular}{llll}
     & $k_P$ & $T_I$ & $T_D$  \\[0.3cm] \hline
 P   & $\frac{T_1}{kT_d}$  & -  & - \\[0.3cm]
 PI  & $\frac{0.9 T_1}{KT_d}$  & $3.3T_d$ &  -\\[0.3cm]
 PID & $\frac{1.2 T_1}{KT_d}$  & $2T_d$  & $0.5T_d$
\end{tabular}
\caption{Table adapted from Leigh, J.R. table 11.1.}
\end{table}

\subsubsection{Assessing Stability}
Now that all the coefficients are determined, we can plot the transfer function as a function of frequency in the complex plane. The easiest way to do this is to expand the complex exponentials as a sum of cosines and sines, collect into the form $a(\omega)+ib(\omega)$ and then plot it as a parametric curve, $(a(\omega),b(\omega))$. Having done that gets the following:

\begin{figure}[H]
    \centering
    
    \caption{ A plot showing the function as a parametric curve over frequencies $\omega=0...10$ and a unit circle. Note that the curve tends to $-\infty$ on the $y$ axis, which corresponds to the integral having infinite gain (an integrator always contributing a phase of $90^{\circ}$) at zero frequency. Note that the curve does not encircle $-1+0i$ as required for stability. The gain margin here is $3.5$dB and the phase margin is $20^{\circ}$. }
    \label{fig:nyquistPlot}
\end{figure}

There are two factors involved with assessing the stability in relation to the Nyquist criterion: gain margin and phase margin. The gain margin (in dB) is a notion of how far away from oscillation the system will be when the frequency is such that the phase lag is exactly $180^{\circ}$, which is expressed as:

$$ g = 20 \log_{10} \left( -Re(H(\omega^*))\right) $$

In order to assess gain margin, we must first find the frequency corresponding to the closest root to the point $-1+0i$ and then plug that frequency, $\omega^*$, into the real part of the transfer function, and then apply the rest of the above formula.

The phase margin is the angle between the $-x$ axis and the point at which the function intersects the unit circle. In other words, it is the difference in phase between the critical point and where the function is magnitude unity (remember that the function must have less than unity gain at phase $180^{\circ}$). In order to assess phase margin, one must first find the frequency at which the magnitude of the transfer function is 1, i.e., $|H(\omega^*)|=1$ (please excuse my abuse of notation from reusing $\omega^*$ for this, they are not otherwise related).  After that, the transfer function should be put in the form $|H|e^{i\phi}$, and then the phase margin will be $180^{\circ} - \phi$. 

\section{In Practise}
If we have done everything up until now correctly, we will expect that the controller will do a few easily identifiable things. First, when we set the set temperature, the measured temperature should approach and overshoot this, and then exhibit first order decay until settling on the set temperature. Second, this should result in some approximately constant (over short periods of time, since over long periods of time the ambient temperature and therefore the level of current required to maintain a certain temperature, will change) amount of current being delivered.

The closed step response should therefore look like this:

\begin{figure}[H]
    \centering
    
    \caption{ Forgive my not labelling the axes, the left axis is temperature in Celsius, and the right is current in amperes. The bottom axis is time in UTC. }
    \label{fig:closedLoopStep}
\end{figure}

\newpage
\section{References and Further Reading}
\begin{enumerate}
    \item Jones, Lucas: Practical Implementation of Temperature Control
    \item Martin, James: Notes on Feedback and Oscillations
    \item Olivi, Martine: The Laplace transform in control theory \\ https://www-sop.inria.fr/apics/sbpi/LtransformOlivi.pdf
    \item Forgan, E.M.: On the use of temperature controllers in cryogenics \\ https://doi.org/10.1016/0011-2275(74)90190-8
    \item Wescott, Tim: Applied Control Theory for Embedded Systems
    \item Leigh, J.R.: Temperature Measurement and Control
\end{enumerate}

\end{document}

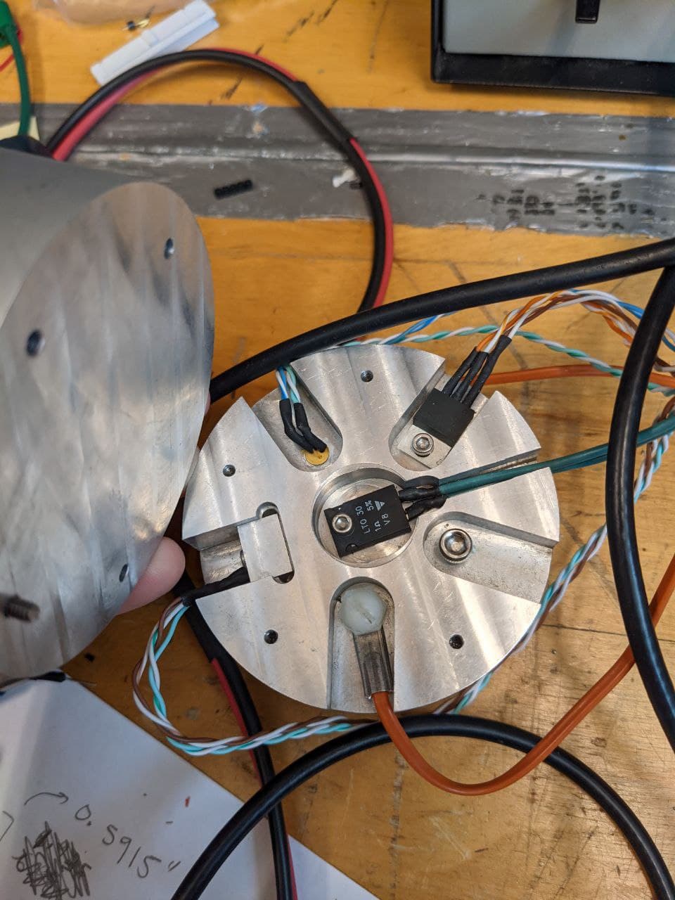
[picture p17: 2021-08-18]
docs/testCellSetup.jpg

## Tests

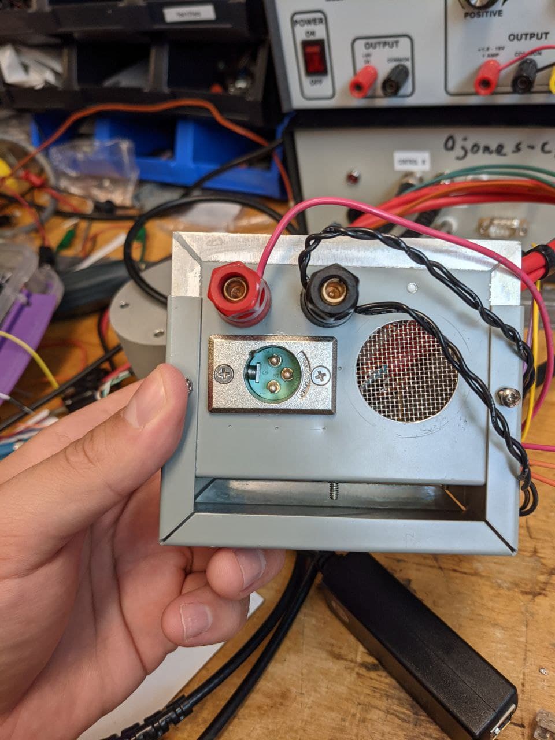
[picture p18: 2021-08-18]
docs/testCellBoxBack.jpg

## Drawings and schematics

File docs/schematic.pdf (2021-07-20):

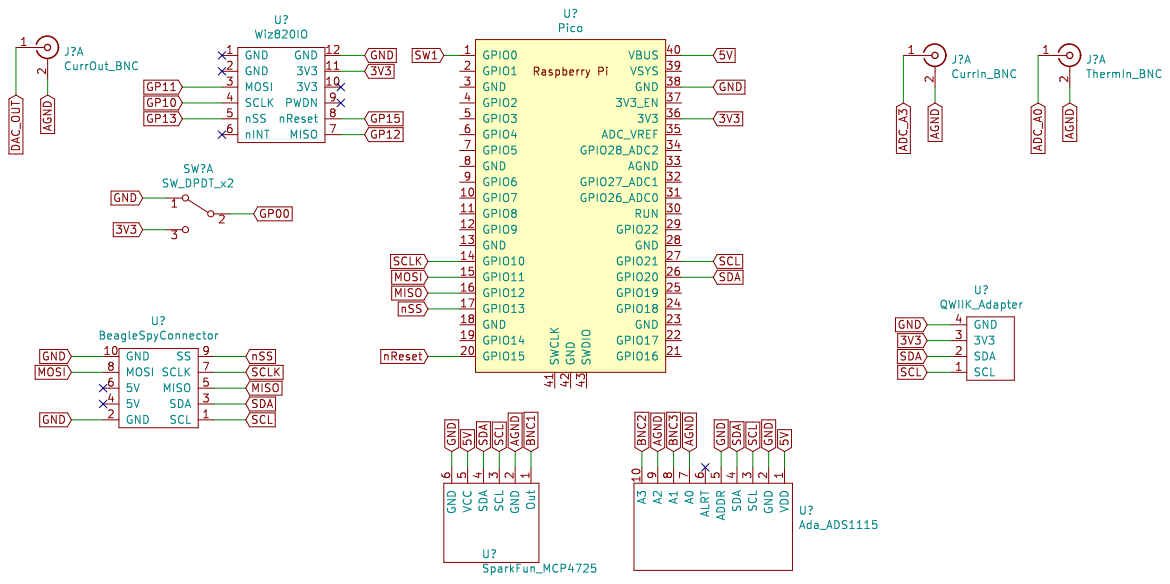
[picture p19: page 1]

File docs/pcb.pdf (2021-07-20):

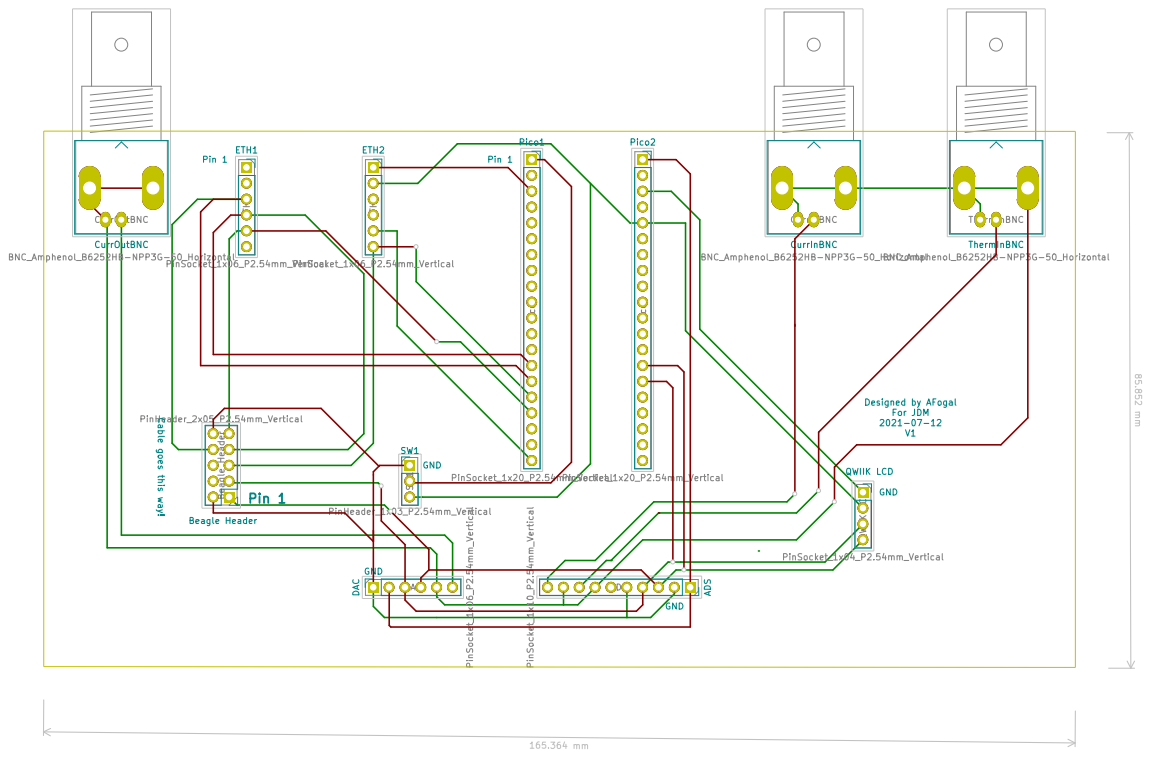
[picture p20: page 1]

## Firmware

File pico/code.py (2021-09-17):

import board
import busio
import digitalio
import time
from adafruit_wiznet5k.adafruit_wiznet5k import WIZNET5K
import adafruit_wiznet5k.adafruit_wiznet5k_socket as socket
from busio import I2C
import adafruit_minimqtt.adafruit_minimqtt as MQTT
import json
import math
import adafruit_mcp4725
import adafruit_ads1x15.ads1115 as ADS
from adafruit_ads1x15.ads1x15 import Mode
from adafruit_ads1x15.analog_in import AnalogIn
from adafruit_bus_device.i2c_device import I2CDevice

##### Constants ############################

# I2C bus stuff (dac/lcd/adc)
i2c_scl = board.GP21
i2c_sda = board.GP20
dac_addr = 0x60
lcd_addr = 0x72
adc1_addr = 0x48
adc2_addr = 0x49

# SPI bus stuff (eth)
SPI1_SCK = board.GP10
SPI1_TX = board.GP11
SPI1_RX = board.GP12
SPI1_CSn = board.GP13
W5500_RSTn = board.GP15

# eth config
MY_MAC = (0x00, 0x01, 0x02, 0x03, 0x04, 0x05)
IP_ADDRESS = (192, 168, 1, 111)
SUBNET_MASK = (255, 255, 255, 0)
GATEWAY_ADDRESS = (192, 168, 1, 1)
DNS_SERVER = (8, 8, 8, 8)
REMOTE_PORT = 5005

# Some pin setup
led = digitalio.DigitalInOut(board.GP25)
led.direction = digitalio.Direction.OUTPUT

ethernetRst = digitalio.DigitalInOut(W5500_RSTn)
ethernetRst.direction = digitalio.Direction.OUTPUT

cs = digitalio.DigitalInOut(SPI1_CSn)
spi_bus = busio.SPI(SPI1_SCK, MOSI=SPI1_TX, MISO=SPI1_RX)

# Default settings (see README)
defaultSettings = {'setCurrent':0, 'setTemp' : 28, 'Kc': 6.7087, 'Ti':330, 'Td':0, 'I_max':4, 'loadResist':1, 'maxTemp':150, 'maxCurr':2.0, 'maxResVolt':5, 'maxRes':13,
                   'maxSuppCurrVolt':5, 'maxSuppCurr':2, 'thermBeta':3380, 'thermR25':10, 'outputToggle':1, 'filterHz':1, 'period':0.016666667,
                   'constCurr':False, 'maxErrorLen':100, 'freqAnalysis':False, 'reportMode':'mean', 'user':'pico', 'password':'password',
                   'serverIP':"192.168.1.103", 'mqttDelay':5e8, 'mqttReconn':300e8, 'lcdRefresh':2.5e8  }
# Attempt to load last used settings
try:
    with open('settings.json', 'r') as settings_file:
        defaultSettings = json.load(settings_file)
        loaded = True
except:
    loaded = False
    

# PID variables
P_Signal = 0
I_Signal = 0
Erorr_Signal = 0
TemperatureDetents = 10 # gives a resolution of 0.1 DegC
CurrentDetents = 100 # gives a resolution of 0.01 A
Error_Sample_Value = []
Error_Sample_Time = []

##### Functions ############################

# Writing a string to the LCD
def lcd_str(device, outs, clear=True):
    with device as lcd:
        if clear: lcd.write(bytes([0x7C, 0x2D]))
        time.sleep(1. / 1000.)  # 1ms in between writes
        lcd.write(bytes([ord(i) for i in list(outs)]))
        time.sleep(1./1000.)


# Run automatically when an MQTT message is recieved
def do_command(client, topic, message):
    #lcd_str(lcd, message)
    
    jc = json.loads(message)
    
    if jc['command'] == "ping":
        client.publish(f"{defaultSettings['user']}/feeds/ack", "PONG")
    elif jc['command'] == "settemp":
        defaultSettings['setTemp'] = math.floor(jc['temp'] * TemperatureDetents) / TemperatureDetents
        I_Signal = 0 #defaultSettings['setCurrent'] * defaultSettings['setCurrent'] * defaultSettings['loadResist']
        defaultSettings['constCurr'] = False
        saveSettings()
    elif jc['command'] == "setcurr":
        defaultSettings['setCurrent'] = math.floor(jc['curr'] * CurrentDetents) / CurrentDetents
        defaultSettings['constCurr'] = True
        saveSettings()
    elif jc['command'] == "toggleOutput":
        if updateLcd == 0 and defaultSettings['outputToggle'] == 0:
            updateLcd = 1 # clears current error and allows continued operation without rebooting

        defaultSettings['outputToggle'] = not defaultSettings['outputToggle'] #jc['toggle']
        saveSettings()
        
    # probably do something and then conditionally ack?
    client.publish(f"{defaultSettings['user']}/feeds/ack", "ACK")

def Kohm_to_Celsius (Thermistor_Resistance):
    if (Thermistor_Resistance <= 0):
        return 0
    Celsius = (defaultSettings['thermBeta'] / (math.log(Thermistor_Resistance / defaultSettings['thermR25']) + defaultSettings['thermBeta'] / 298)) - 273
    return Celsius
    
    
def saveSettings():
    try:
        with open("settings.json", "w") as outfile:
            json.dump(defaultSettings, outfile)
    except:
        pass
    
def mean(l):
    s = 0
    c = 0
    
    if not (len(l)>0):
        return 0
    
    for i in l:
        s += i
        c += 1
        
    return s/c

##### Setup ############################

# i2c bus and lcd init, show splash
i2c_bus = I2C(i2c_scl, i2c_sda, frequency=100000)
lcd = I2CDevice(i2c_bus, lcd_addr)#, probe=False)
lcd_str(lcd, "PID Temp Control V1.0")
# lcd_bytes(i2c_bus, [0x0A]) # Sets text as splash
time.sleep(0.5)

# DAC and ADC setup
dac = adafruit_mcp4725.MCP4725(i2c_bus, address=dac_addr)
dac.value = 0
time.sleep(0.01)
ads = ADS.ADS1115(i2c_bus, address=adc1_addr)
curr_adc = AnalogIn(ads, ADS.P2, ADS.P3)
therm_adc = AnalogIn(ads, ADS.P0, ADS.P1)
#ads.mode = Mode.CONTINUOUS # this breaks everything
ads.data_rate = 860 # Max rate is 860

# ads2 = ADS.ADS1115(i2c_bus, address=adc2_addr)
# curr_adc = AnalogIn(ads2, ADS.P0)
# ads2.data_rate = 860

# First ADC channel read in continuous mode configures device
# and waits 2 conversion cycle
_ = curr_adc.value
_ = therm_adc.value

# Reset W5500 first
ethernetRst.value = False
time.sleep(0.1)
ethernetRst.value = True

# Initialize ethernet interface without DHCP
eth = WIZNET5K(spi_bus, cs, is_dhcp=False, mac=MY_MAC)

# Set network configuration
eth.ifconfig = (IP_ADDRESS, SUBNET_MASK, GATEWAY_ADDRESS, DNS_SERVER)
socket.set_interface(eth)

#eth._debug = True
MQTT.set_socket(socket, eth)
time.sleep(1)
mqtt_client = MQTT.MQTT(defaultSettings['serverIP'], username=defaultSettings['user'], password=defaultSettings['password'], is_ssl=False, port=REMOTE_PORT, keep_alive=5)
mqtt_client.on_message = do_command

try:
    mqtt_client.connect(clean_session=False)
    time.sleep(0.01)
    mqtt_client.subscribe("server/feeds/commands", qos=1)
    time.sleep(0.01)
    conn = True
    ethi = True
except RuntimeError: # broker not online
    conn = False
    ethi = True
except AssertionError: # no cable
    conn = False
    ethi = False

# Display IP if everything ok
space = ''.join([" " for i in range(8)])
if conn:
    lcd_str(lcd, f"INET OK {space}{eth.pretty_ip(eth.ip_address)}")
elif ethi:
    lcd_str(lcd, "No Broker!")
else:
    lcd_str(lcd, "No eth!")
time.sleep(0.8)

if loaded:
    lcd_str(lcd, "Loaded Last Settings")
else:
    lcd_str(lcd, "Didn't load last settings")
time.sleep(0.5)

first = True
counter = 0
Bad_Frame_Counter = 0
updateLcd = 1
Last_Temperature = -999
report_temps = []
report_currs = []
t_last = time.monotonic_ns()
t_conn = time.monotonic_ns()
t_frame = time.monotonic_ns()
t_lcd = time.monotonic_ns()
while True:
    
    # time variables
    t_curr = time.monotonic_ns()
    t_delta = t_curr - t_last
    frame_duration = (t_curr - t_frame) / 1e9
    
    if t_delta > defaultSettings['mqttDelay'] and conn:  # 5 sec
        try: # I think this throws socket.timeout error
            mqtt_client.loop(timeout=0.001) # polling for commands
            
            if defaultSettings['reportMode'] == 'latest':
                mqtt_client.publish(f"{defaultSettings['user']}/feeds/state", json.dumps({"temp" :Actual_Temperature, "curr":Control_Signal_Amps, "state":defaultSettings }))
                report_temps = []
                report_currs = []
            elif defaultSettings['reportMode'] == 'mean':
                if len(report_temps) > 0: 
                    mqtt_client.publish(f"{defaultSettings['user']}/feeds/state", json.dumps({"temp" :mean(report_temps), "curr":mean(report_currs), "state":defaultSettings }))
                    report_temps = []
                    report_currs = []
            conn = True
            ethi = True
            t_conn = t_curr
        except MQTT.MMQTTException: # broker offline
            conn = False
            ethi = True
            t_conn = t_curr
        except AssertionError: # no cable
            conn = False
            ethi = False
            t_conn = t_curr
            
        t_last = t_curr
        
    # retries connection every 30s, can take a very long time
    if t_curr - t_conn > defaultSettings['mqttReconn'] and not conn: # 30s
        try:
            mqtt_client.connect(clean_session=False)
            time.sleep(0.01)
            mqtt_client.subscribe("server/feeds/commands", qos=1)
            time.sleep(0.01)
            conn = True
            ethi = True
            t_conn = t_curr
        except RuntimeError: # broker offline
            conn = False
            ethi = True
            t_conn = t_curr
        except AssertionError: # no cable
            conn = False
            ethi = False
            t_conn = t_curr
            
    if frame_duration >= defaultSettings['period']:
        # read inputs: (PCB has the differentials backwards...)
        Supply_Current_Voltage = -curr_adc.voltage
        actResVolt = -therm_adc.voltage

        # Get current state
        #Actual_Resistance = defaultSettings['maxRes'] * actResVolt / defaultSettings['maxResVolt']
        #if (Actual_Resistance == defaultSettings['thermR25']):
        #    Actual_Temperature = 25
        #elif ((Actual_Resistance <= 0) or (Actual_Resistance > defaultSettings['maxRes'])):
        #    Actual_Temperature = 0
        #else:
        #    Actual_Temperature = Kohm_to_Celsius(Actual_Resistance)
        
        # for lm335 in the little box
        Actual_Temperature = actResVolt * 100

        Supply_Current = defaultSettings['maxSuppCurr'] * Supply_Current_Voltage / defaultSettings['maxSuppCurrVolt']

        Error_Sample_Value.append(defaultSettings['setTemp'] - Actual_Temperature)
        Error_Sample_Time.append(time.monotonic_ns())

        # Now go through the list and add up the values with an exponential weighting function
        Error_Signal = 0
        Total_Weight = 0
        for i in range(len(Error_Sample_Value)):
            # find the time in seconds between when this data point was acquired, and present time
            Relative_Time = (Error_Sample_Time[-1] - Error_Sample_Time[i]) / 1e9
            Sample_Weight = math.exp(- Relative_Time / defaultSettings['filterHz'])
            Error_Signal += Sample_Weight * Error_Sample_Value[i]
            Total_Weight += Sample_Weight
        Error_Signal /= Total_Weight

        if (len(Error_Sample_Value) >= defaultSettings['maxErrorLen']):
            del Error_Sample_Value[0]
            del Error_Sample_Time[0]
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

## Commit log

2021-06-18 Added adc/dac testing code just in case I want it again later
2021-06-18 updated testing code to check voltage conversion
2021-06-23 Added schematic and pcb layout prototype (and the whole kicad project, really)
    [PID-controller-pcb.kicad_pcb, PID-controller-pcb.sch]
2021-06-29 touched up pcb, added a comment in code.py
    [PID-controller-pcb-B_Cu.gbr, PID-controller-pcb-B_Mask.gbr, PID-controller-pcb-B_Paste.gbr, PID-controller-pcb-B_SilkS.gbr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]
2021-07-05 added screw holes on PCB
    [PID-controller-pcb-B_Cu.gbr, PID-controller-pcb-B_Mask.gbr, PID-controller-pcb-B_Paste.gbr, PID-controller-pcb-B_SilkS.gbr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]
2021-07-05 added more screw holes on PCB
    [PID-controller-pcb-B_Cu.gbr, PID-controller-pcb-B_Mask.gbr, PID-controller-pcb-B_Paste.gbr, PID-controller-pcb-B_SilkS.gbr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]
2021-07-06 added D control, tuned, limited I
    [tograph.csv]
2021-07-07 removed old data
    [tograph.csv]
2021-07-08 more tuning
    [toplot.csv]
2021-07-09 added switch to pcb layout
    [PID-controller-pcb-B_Cu.gbr, PID-controller-pcb-B_Mask.gbr, PID-controller-pcb-B_Paste.gbr, PID-controller-pcb-B_SilkS.gbr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]
2021-07-09 removed all data
    [toplot.csv]
2021-07-12 seperated grounds, slightly reworked design
    [PID-controller-pcb-B_Cu.gbr, PID-controller-pcb-B_Mask.gbr, PID-controller-pcb-B_Paste.gbr, PID-controller-pcb-B_SilkS.gbr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]
2021-07-14 added beagle spy breakout for spi and i2c, didnt route pins 4 or 6 (used for powering device) as we do not want 5V power for spi or i2c
    [PID-controller-pcb-B_Cu.gbr, PID-controller-pcb-B_Mask.gbr, PID-controller-pcb-B_Paste.gbr, PID-controller-pcb-B_SilkS.gbr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]
2021-07-14 slightly simplified board traces
    [PID-controller-pcb-B_Cu.gbr, PID-controller-pcb-B_Mask.gbr, PID-controller-pcb-B_Paste.gbr, PID-controller-pcb-B_SilkS.gbr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]
2021-07-17 updated pcb gerbers
    [PID-controller-pcb-B_Cu.gbr, PID-controller-pcb-B_Mask.gbr, PID-controller-pcb-B_Paste.gbr, PID-controller-pcb-B_SilkS.gbr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]
2021-07-20 updated schematic and pcb pdfs
    [PID-controller-pcb.kicad_pcb, PID-controller-pcb.sch]
2021-07-21 partial box drawing done in qcad
    [pid-controller-box.dxf]
2021-07-23 updated drawing
    [pid-controller-box.dxf]
2021-07-30 tested pcb and poe router
2021-07-30 Tweaked pcb to make version 2 with fixed grounding and correctly oriented differentials
    [PID-controller-pcb-B_Cu.gbr, PID-controller-pcb-B_Mask.gbr, PID-controller-pcb-B_Paste.gbr, PID-controller-pcb-B_SilkS.gbr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]
2021-08-03 Redesigned board for PoE
    [PID-controller-pcb-B_Cu.gbr, PID-controller-pcb-B_Mask.gbr, PID-controller-pcb-B_Paste.gbr, PID-controller-pcb-B_SilkS.gbr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]
2021-08-03 updated box for PoE with adafruit jack
    [pid-controller-box.dxf]
2021-08-04 slightly tweaked box to make sure eth jack has enough room, added a way to continue after current error
    [pid-controller-box.dxf]
